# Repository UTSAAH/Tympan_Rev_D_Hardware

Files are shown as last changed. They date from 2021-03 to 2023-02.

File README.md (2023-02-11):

D_Tympan_DFMI_1.0 consisits of PCB design files catering to the requirements of Indian PCB Manufacturers. 

The following are the changes done in the PCB design files (.pcb file):  

	1.Four layered board with power/gnd planes as follows:
		Top Cu - GND plane   
		Second layer(In. Cu 1) - None  
		Third layer(In. Cu 2) - 3.3 V power plane  
		Bottom Cu - GND plane  
	2.Details about vias:  
		Through hole vias - 0.6mm/0.4mm  
		Blind vias ( In. Cu 2 - B. Cu) - 0.45mm/ 0.15mm  
	3. Changes in component placement:  
		R20, R23 - Moved from B. Cu to F. Cu layer  
		C14, C20, C21, C22,C34 - Moved from B. Cu to F. Cu layer  

The objectives for design changes in Tympan Rev D, the test results and the outcomes were presented at International HEaring Aid Reserach Conference IHCOn 2022 and the same poster 'IHCON 2022 poster_Dhwani(Tympan DFMI) is uploaded.

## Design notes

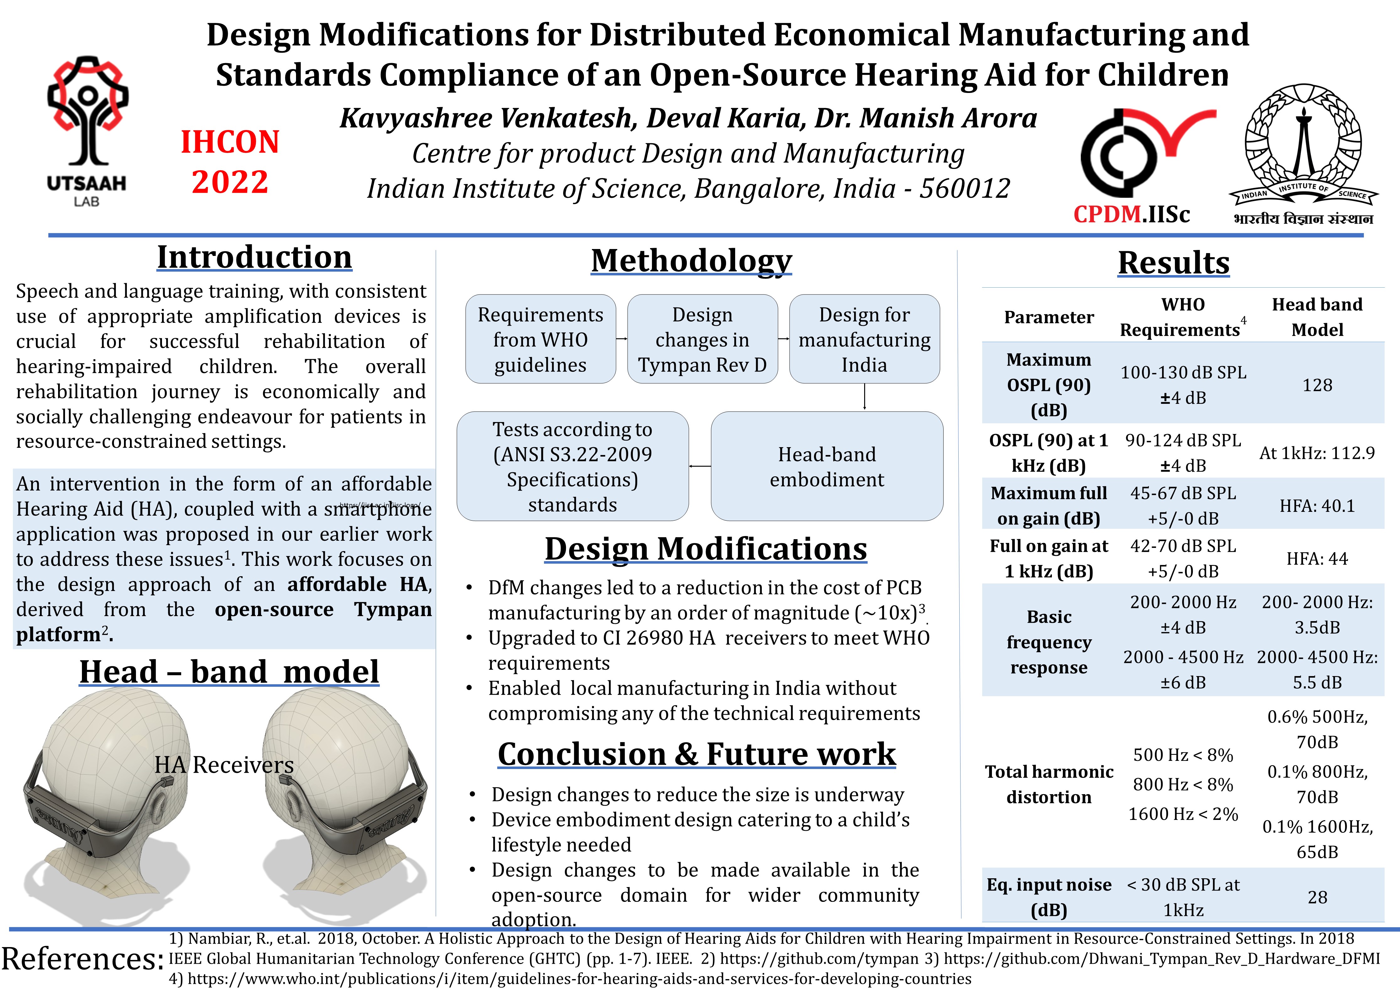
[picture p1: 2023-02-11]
IHCON 2022 Poster_Dhwani(TympanDFMI).jpg

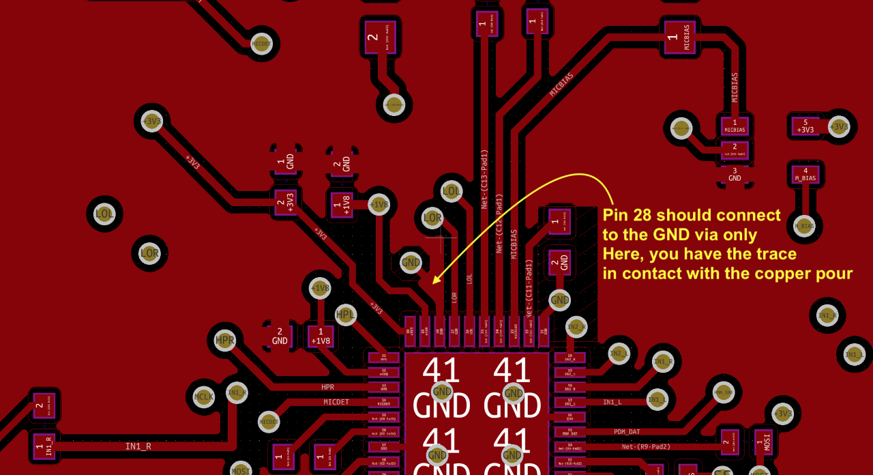
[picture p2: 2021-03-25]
Review4_25th march_Pin 28 routing.png

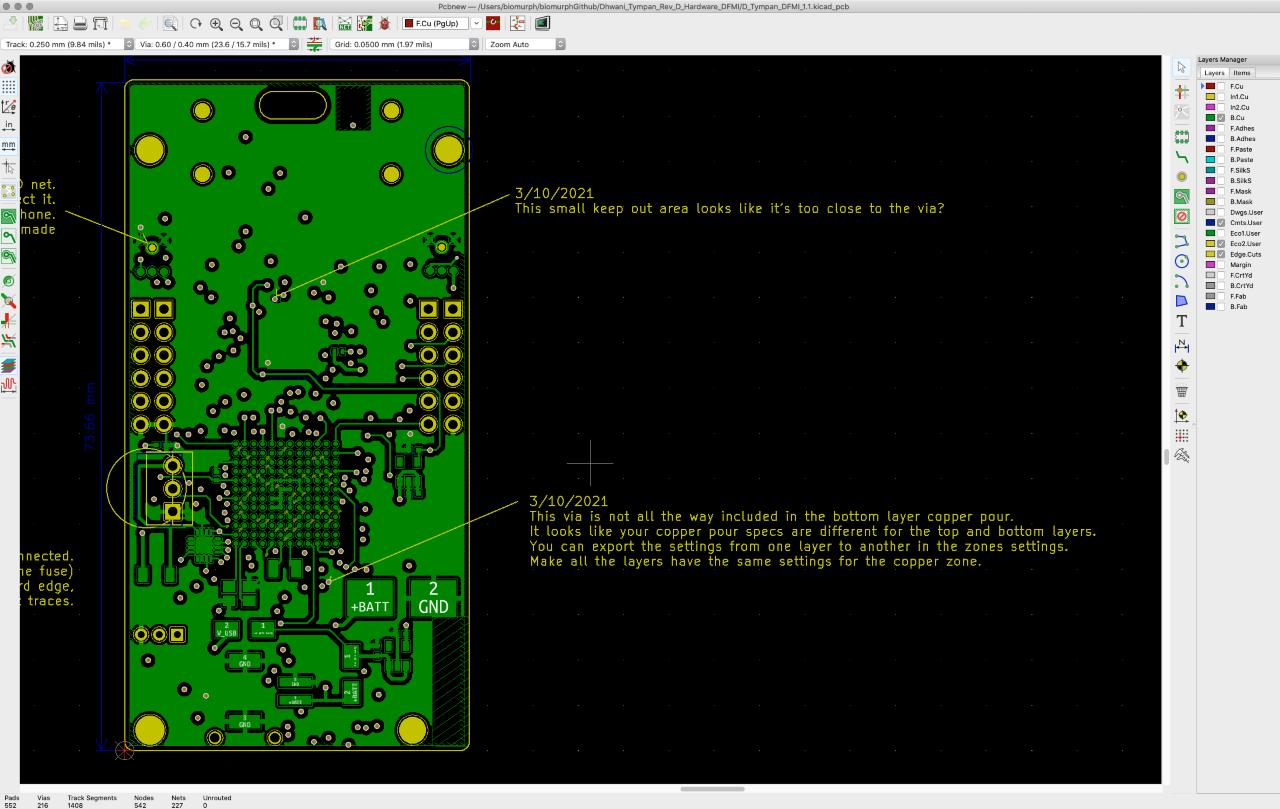
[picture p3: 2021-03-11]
Review2- 10th March 2021.png

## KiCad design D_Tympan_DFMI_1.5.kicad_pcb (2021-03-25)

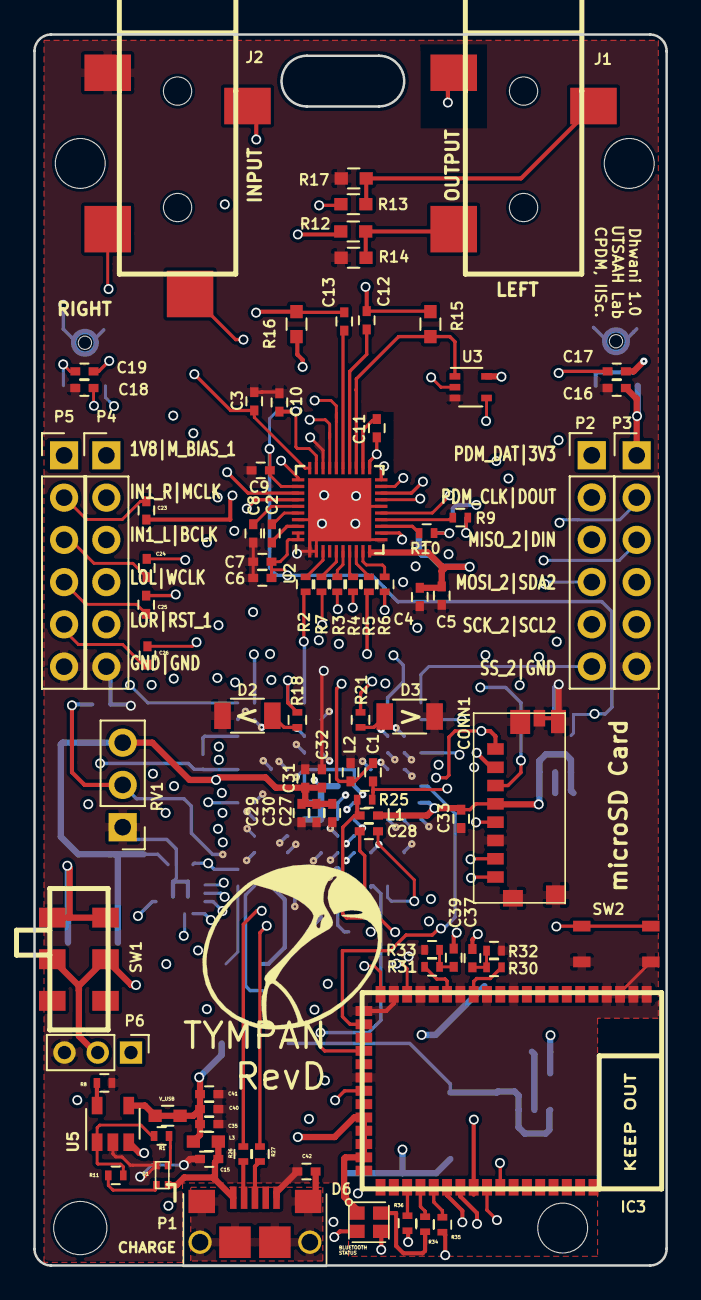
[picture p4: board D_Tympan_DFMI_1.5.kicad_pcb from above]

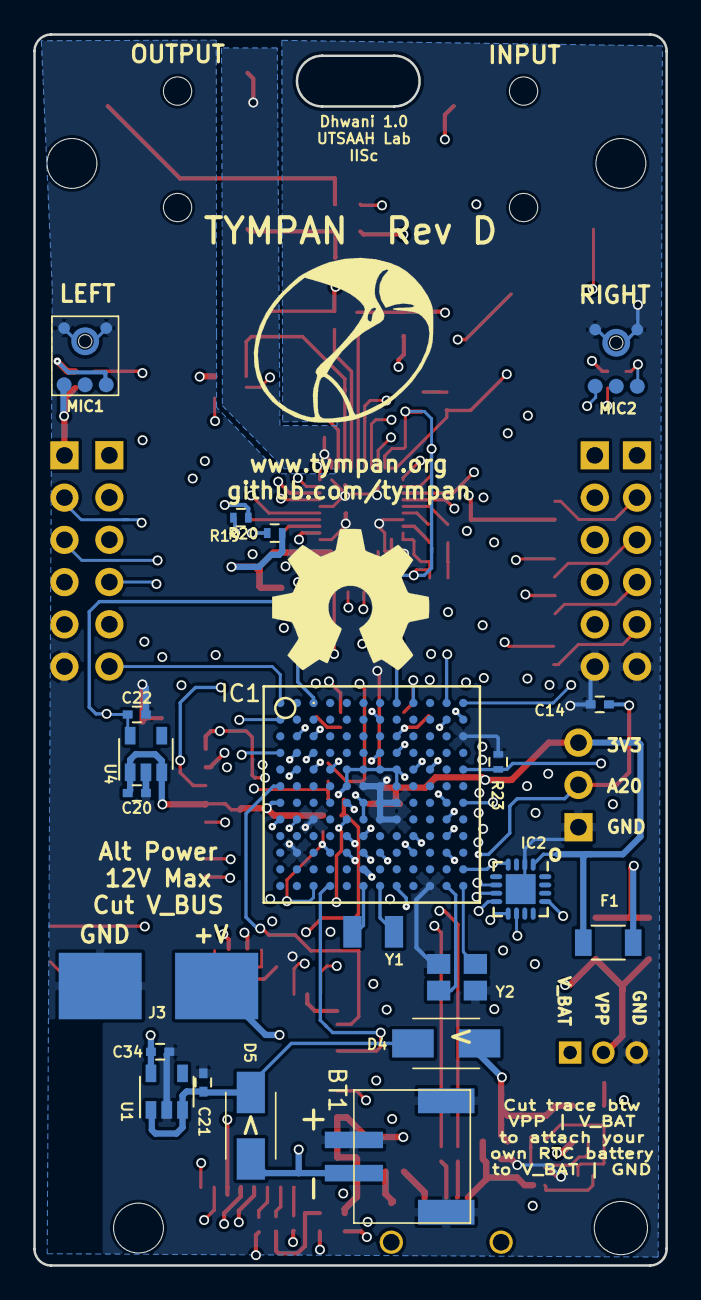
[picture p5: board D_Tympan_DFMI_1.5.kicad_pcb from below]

Board: 4 copper layers, 38.0 x 74.0 mm, 113 parts (21 on the bottom side), 117 nets.

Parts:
BT1: 4UCON-20519; 4UCON-0217-20519
C1, C3, C5, C7, C10, C14, C16, C18, C28, C29, C42: 0.1uF; C_0402
C2, C8, C12, C13, C23, C24, C25, C26, C27, C32, C33, C37, C39: 2.2uF; C_0402
C4, C6, C11, C15: 10uF; C_0402
C9, C17, C19, C20, C21, C22, C34: 1uF; C_0402
C30, C31: 10nF; C_0402
C35: 4.7uF; C_0402
C40: 15pF; C_0402
C41: 22nF; C_0402
CONN1: 8_PIN_microSD; MOLEX_47571-0001
D1: APHB1608SGNC; ABHB1608S
D2, D3: LED; C_1206
D4, D5: Shottkey; ACDBA340-HF
D6: Led_RGB_CA; CLMVB-FKA-CFHEHLCBB7a363
F1: FUSE; C_1206
IC1: MK66FX1M0VMD18; BGA-144-1mm
IC2: MKL02Z32VFG4; QFN-16-1EP_3x3mm_Pitch0.5mm
IC3: BC127
J1: SJ-3523-SMT-TR
J2: SJ-3524-SMT-TR-PI; SJ-3524-SMT-TR
J3: alt Power Pads
L1, L2: 600R; C_0402
L3: 1K; C_0603
MIC1, MIC2: SPM0687LR5H-1
P1: USB_OTG; 10118193_microUSB
P2, P3, P4, P5: CONN_01X06; Pin_Header_Straight_1x06_Pitch2.54mm
P6: CONN_01X03; Pin_Header_Straight_1x03_Pitch2.00mm
P7: CONN_01X01; NPTH_2.4mm
P8, P9, P10: CONN_01X01; NPTH_3.2mm
R1, R11, R19, R20, R32, R33: 1K; R_0402
R2, R3, R4, R5, R6, R7, R9, R10, R26, R27: 33R; R_0402
R8: 2.2K; R_0402
R12, R13: 0R; C_0603
R14, R17: DNP; C_0603
R15, R16: 2.2K; C_0603
R18, R21, R34, R35, R36: 240R; R_0402
R23: 100K; R_0402
R25: 470R; R_0402
R30, R31: 10K; R_0402
RV1: POT; Pin_Header_Straight_1x03_Pitch2.54mm
SW1: CL-SB-22A
SW2: TACT_SWITCH; PTS810
U1: AP2210K-3.3TRG1; SOT-23-5
U2: TLV320AIC3206IRSBT; UQFN-40-1EP_5x5mm_Pitch0.4mm
U3: 74LVC1G66; SOT-353_SC-70-5
U4: LP5907MFX-1.8; SOT-23-5
U5: MCP73831; SOT-23-5
V_USB: DNP; C_0603
Y1: 32.768kHz; LFXTAL009678
Y2: 16MHz; FA_238_16.0000MB_K3

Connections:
+1V8: C6.1, C7.1, C9.1, C10.1, C22.1, P5.1, U2.29, U2.32, U2.39, U2.40, U4.5
+3V3: C3.2, C4.2, C5.2, C16.2, C18.2, C20.1, C27.1, C29.1, C30.1, C31.1, C32.1, C33.1, CONN1.4, D6.1, F1.2, IC1.E5, IC1.E6, IC1.E7, IC1.E8, IC1.F5, IC1.F8, IC1.G1, IC2.1, IC3.30, IC3.31, IC3.32, IC3.33, L1.2, MIC1.4, MIC2.4, P3.1, R19.1, R20.1, RV1.3, U2.10, U2.30, U3.5, U4.1, U4.3
+BATT: BT1.1, D5.2, J3.1, U5.3
/BCLK: IC1.A11, P4.3, R3.1
/BT_CTS: IC1.M8, IC3.40
/BT_PIO0: IC1.F1, IC3.23
/BT_PIO5: IC1.M4, IC3.25
/BT_RTS: IC1.K4, IC3.43
/BT_RX: IC1.E9, IC3.42
/BT_TX: IC1.E10, IC3.41
/BT_nRESET: IC1.K5, IC3.44
/CLK: CONN1.5, IC1.D1
/CMD: CONN1.3, IC1.E4
/DAT0: CONN1.7, IC1.D2
/DAT1: CONN1.8, IC1.D3
/DAT2: CONN1.1, IC1.E2
/DAT3: CONN1.2, IC1.E3
/DIN: IC1.B11, R5.1
/DIN_1: IC1.B12, P3.3
/DOUT: IC1.D8, R6.1
/DOUT_1: IC1.B7, P3.2
/HPL: R12.1, U2.31
/HPR: R13.1, U2.33
/IN1_L: C24.1, C37.1, U2.17
/IN1_R: C23.1, C39.1, U2.18
/IN2_L: C17.1, U2.19
/IN2_R: C19.1, U2.20
/LED_0: IC3.37, R36.1
/LED_1: IC3.38, R34.1
/LED_2: IC3.39, R35.1
/LOL: C25.1, IC3.21, U2.26
/LOR: C26.1, IC3.19, U2.27
/MCLK: IC1.C8, P4.2, R7.1
/MICBIAS: R15.1, U2.23, U3.1
/MICDET: J2.4, U2.34
/MISO_2: IC1.C2, P2.3
/MOSI_2: IC1.C3, P2.4
/M_BIAS: IC1.A3, U3.4
/M_BIAS_1: IC1.H11, P4.1
/PDM_CLK: P2.2, U2.12
/PDM_DAT: P2.1, U2.15
/POT: C14.1, IC1.K11, RV1.2
/PROG: IC2.10, SW2.1, SW2.2
/PTA0: IC1.J5, IC2.8
/PTA1: IC1.J6, IC2.6
/PTA2: IC1.K6, IC2.9
/PTA3: IC1.K7, IC2.7
/RESET_B: IC1.L12, IC2.4, IC2.13
/SCK_2: IC1.B1, P2.5
/SCL2: IC1.K9, P3.5
/SCL/SS: IC1.G12, R10.1, R20.2
/SDA2: IC1.J9, P3.4
/SDA/MOSI: IC1.G11, R9.1, R19.2
/SS_2: IC1.A1, P2.6
/USB: C15.1, D1.3, L3.1, P1.1
/USB0_D+: IC1.H1, R27.2
/USB0_D-: IC1.H2, R26.2
/VREGEN: IC1.E12, IC3.28, R23.1
/V_USB: C35.1, C40.1, C41.1, D4.2, L3.2, U5.4, V_USB.1, V_USB.2
/WCLK: IC1.A12, P4.4, R4.1
/nRESET: IC1.A8, R2.1
/nRESET_1: IC1.J11, P4.5
Earth: C42.2, P1.6, P1.7, P1.8, P1.9, P1.10, P1.11
GND: BT1.2, BT1.3, BT1.4, C3.1, C4.1, C5.1, C6.2, C7.2, C8.2, C9.2, C10.2, C11.2, C14.2, C15.2, C16.1, C18.1, C20.2, C21.2, C22.2, C27.2, C29.2, C30.2, C31.2, C32.2, C33.2, C34.2, C35.2, C40.2, C41.2, C42.1, CONN1.6, CONN1.9, CONN1.10, CONN1.11, CONN1.12, CONN1.13, D1.2, D2.1, D3.1, IC1.C12, IC1.F6, IC1.F7, IC1.G7, IC1.G8, IC1.H3, IC1.H7, IC1.H8, IC1.K2, IC1.M10, IC2.2, IC2.17, IC3.1, IC3.2, IC3.3, IC3.4, IC3.11, IC3.13, IC3.15, IC3.18, IC3.20, IC3.22, IC3.27, J1.1, J2.1, J3.2, L2.2, MIC1.2, MIC1.3, MIC2.2, MIC2.3, P1.5, P3.6, P4.6, P5.6, P6.3, R8.2, R14.2, R17.2, R23.2, R32.2, R33.2, RV1.1, SW2.3, SW2.4, U1.2, U2.1, U2.2, U2.11, U2.16, U2.21, U2.28, U2.37, U2.41, U3.3, U4.2, U5.2, Y2.2, Y2.4
unnamed: C1.1, C28.1, IC1.G6, IC1.H6, L2.1
unnamed: C1.2, IC1.G5, R25.1
unnamed: C2.1, U2.36
unnamed: C2.2, U2.38
unnamed: C8.1, U2.35
unnamed: C11.1, U2.22
unnamed: C12.1, U2.24
unnamed: C12.2, J2.2, R15.2
unnamed: C13.1, U2.25
unnamed: C13.2, J2.3, R16.1
unnamed: C17.2, MIC1.1
unnamed: C19.2, MIC2.1
unnamed: C21.1, D4.1, D5.1, U1.1, U1.3
unnamed: C23.2, P5.2
unnamed: C24.2, P5.3
unnamed: C25.2, P5.4
unnamed: C26.2, P5.5
unnamed: C28.2, IC1.M3
unnamed: C37.2, R30.2, R32.1
unnamed: C39.2, R31.2, R33.1
unnamed: D1.1, R11.1
unnamed: D1.4, R1.1
unnamed: D2.2, R18.2
unnamed: D3.2, R21.2
unnamed: D6.2, R34.2
unnamed: D6.3, R35.2
unnamed: D6.4, R36.2
unnamed: F1.1, SW1.1, SW1.4
unnamed: IC1.A9, R18.1
unnamed: IC1.D7, R21.1
unnamed: IC1.H5, L1.1, R25.2
unnamed: IC1.M6, Y1.1
unnamed: IC1.M7, Y1.2
unnamed: IC1.M11, Y2.1
unnamed: IC1.M12, Y2.3
unnamed: IC3.14, R30.1
unnamed: IC3.16, R31.1
unnamed: J1.2, R12.2, R14.1
unnamed: J1.3, R13.2, R17.1
unnamed: P1.2, R26.1
unnamed: P1.3, R27.1
unnamed: R1.2, R11.2, U5.1
unnamed: R2.2, U2.3
unnamed: R3.2, U2.6
unnamed: R4.2, U2.7
unnamed: R5.2, U2.8
unnamed: R6.2, U2.9
unnamed: R7.2, U2.5
unnamed: R8.1, U5.5
unnamed: R9.2, U2.14
unnamed: R10.2, U2.13
unnamed: R16.2, U3.2
VPP: C34.1, IC1.L6, P6.1, P6.2, SW1.2, SW1.5, U1.5

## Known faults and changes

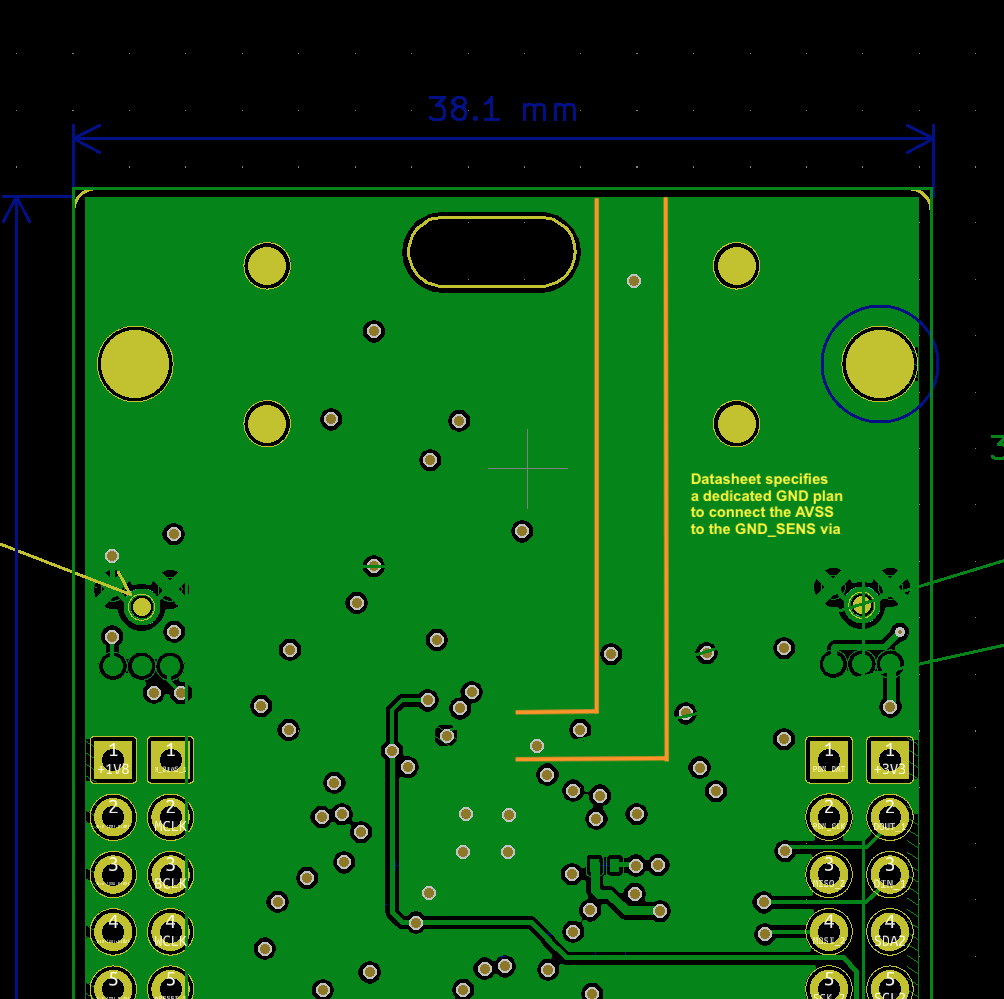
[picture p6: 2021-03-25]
Review3- 18th March 21-GND Issue DFMI Bottom.png

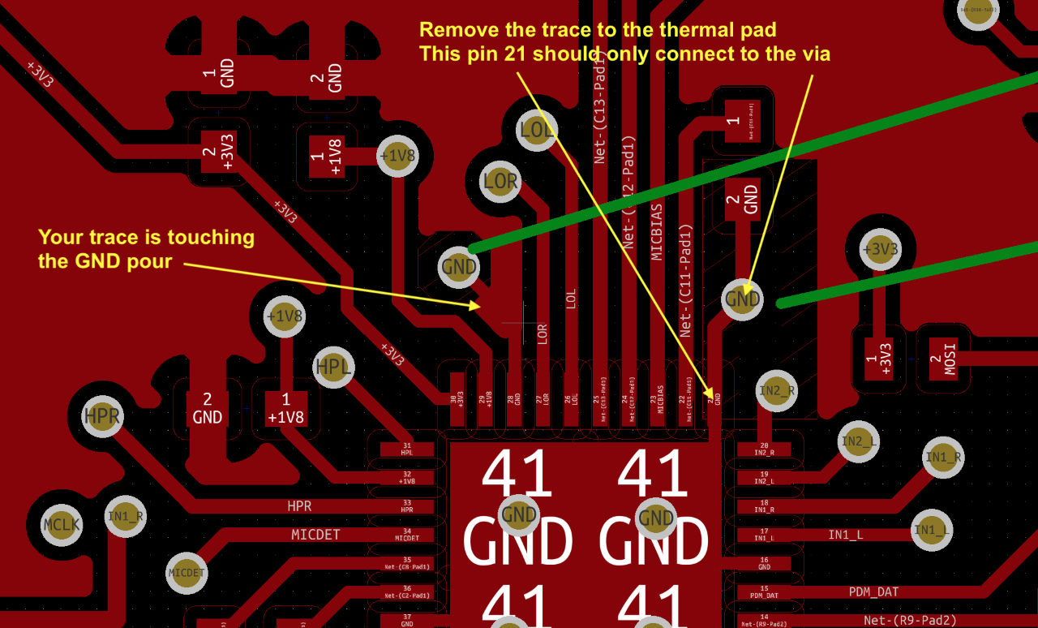
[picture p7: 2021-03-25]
Review3- 18th March 21-GND Issue DFMI Top.png

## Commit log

2021-03-11 Add files via upload
    Response to review on 10th March 2021
    1. Corrections in Keep out area
    2. Homogenizing zone properties
    [D_Tympan_DFMI_1.2.kicad_pcb]
2021-03-18 Add files via upload
    Corrections in GND SENS and AVSS
    [D_Tympan_DFMI_1.3.kicad_pcb]
2021-03-25 Add files via upload
    1.Created dedicated GND plane for GND_SENS and AVSS
    2. Other corrections related to Thermal pad and GND as suggested during last review
    [D_Tympan_DFMI_1.4.kicad_pcb]
2021-03-25 Add files via upload
    Corrections in pin 28 connection -connected only to GND via, isolated the trace from rest of the copper pour.
    [D_Tympan_DFMI_1.5.kicad_pcb]
